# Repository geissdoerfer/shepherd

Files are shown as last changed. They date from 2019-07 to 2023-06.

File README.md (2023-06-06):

# SHEpHERD: SyncHronized Energy Harvesting Emulator RecorDer



DEPRECATION NOTICE:
This repository has been deprecated in favor of [the next generation of Shepherd](https://github.com/orgua/shepherd).

Batteryless sensor nodes depend on harvesting energy from their environment.
Developing solutions involving groups of batteryless nodes requires a tool to analyze, understand and replicate spatio-temporal harvesting conditions.
*shepherd* is a testbed for the batteryless Internet of Things, allowing to record harvesting conditions at multiple points in space over time.
The recorded data can be replayed to attached wireless sensor nodes, examining their behaviour under the constraints of spatio-temporal energy availability.

**Features**

 - High-speed, high resolution current and voltage sensing
 - Technology-agnostic: Currently, solar and kinetic energy harvesting are supported
 - Remote programming/debugging of ARM Cortex-M MCUs using Serial-Wire-Debug
 - High resolution, synchronized GPIO tracing
 - Configurable, constant voltage power supply for attached sensor nodes
 - Level-translated serial connection to the attached sensor nodes

For a detailed description see our [Paper](https://wwwpub.zih.tu-dresden.de/~mzimmerl/pubs/geissdoerfer19shepherd.pdf).

A *shepherd* instance consists of a group of spatially distributed *shepherd* nodes that are time-synchronized with each other.
Each *shepherd* node consists of a [BeagleBone](https://beagleboard.org/bone), the *shepherd* cape and a particular choice of capelets according to the user requirements.

This repository contains the hardware design files for the shepherd cape and the various capelets, the software running on each *shepherd* node as well as the tool to orchestrate a group of *shepherd* nodes connected to a network.

## Quickstart

Start by assembling your *shepherd* nodes, consisting of a BeagleBone Green/Black, a *shepherd* cape, a harvesting capelet and a target capelet.
The next step is to manually install the latest Ubuntu Linux on each BeagleBone.
You can install it to SD-card or the on-board EMMC flash, following [the official instructions](https://elinux.org/BeagleBoardUbuntu).
Make sure to follow the instructions for **BeagleBone**.

The following instructions describe how to install the *shepherd* software on a group of *shepherd* nodes connected to an Ethernet network.
We assume that your local machine is connected to the same network, that the nodes have internet access and that you know the IP address of each node.

If you haven't done it yet, clone this repository to your local machine:

```
git clone https://github.com/geissdoerfer/shepherd.git
```

Next, install the tools used for installing and controlling the *shepherd* nodes.
We'll use [Ansible](https://www.ansible.com/) to remotely roll out the basic configuration to each *shepherd* node and *shepherd-herd* to orchestrate recording/emulation across all nodes.
The tools are hosted on `PyPI` and require Python version >= 3.6.
You'll also need to have `sshpass` installed on your machine, which is available through the package management system of all major distributions.
Install the tools using `pip`:

```
pip3 install ansible shepherd-herd
```

The `inventory/herd.yml` file shows an example of how to provide the host names and known IP addresses of your BeagleBones.
Adjust it to reflect your setup.
You can arbitrarily choose and assign the hostnames (sheep0, sheep1, in this example) and the ansible_user (jane in this example).

```
sheep:
  hosts:
    sheep0:
        ansible_host: 192.168.1.100
    sheep1:
        ansible_host: 192.168.1.101
    sheep2:
        ansible_host: 192.168.1.102
  vars:
    ansible_user: jane
```

Now run the `bootstrap.yml` *Ansible* playbook, which sets the hostname, creates a user and enables passwordless ssh and sudo:

```
ansible-playbook deploy/bootstrap.yml
```

Finally, use the `install.yml` playbook to setup the *shepherd* software, optionally configuring PTP for time-synchronization:

```
ansible-playbook deploy/install.yml -e ptp=true
```

## Usage

Record two minutes of data:

```
shepherd-herd record -l 120 -o recording.h5
```
The command starts the recording asynchronously and returns after all nodes have started recording.
While the nodes are still recording (indicated by blinking of LED 1 and 2), prepare a directory on your local machine:

```
mkdir ~/shepherd_recordings
```

After the nodes stop blinking, you can retrieve the data to analyze it on your local machine:

```
shepherd-herd retrieve recording.h5 ~/shepherd_recordings
```

After installing some additional dependencies, you can use the provided command line utility from `extra/plot.py` to visualize the recorded data:

```
pip install numpy matplotlib h5py click
python extra/plot.py -f ~/shepherd_recordings/sheep1/rec.h5
```

For a detailed description of the [HDF5](https://en.wikipedia.org/wiki/Hierarchical_Data_Format) based data format, refer to the [corresponding documentation](https://shepherd-testbed.readthedocs.io/en/latest/user/data_format.html).

Finally, replay the previously recorded data to the attached sensor nodes, recording their power consumption:

```
shepherd-herd emulate -o consumption.h5 recording.h5
```

Try `shepherd-herd --help` or check out the documentation [here](https://shepherd-testbed.readthedocs.io/en/latest/user/cli.html#shepherd-herd) for a list of all options.

## Problems and Questions

*shepherd* is an early stage project and chances are that something is not working as expected.
Also, some features are not yet fully supported or documented.
If you experience issues or require additional features, please get in touch via e-mail or by creating an issue on github.

## Documentation

The documentation is hosted on [readthedocs](https://shepherd-testbed.readthedocs.io/en/latest/).

## People

*shepherd* development is lead at the Networked Embedded Systems Lab at TU Dresden as part of the DFG-funded project Next-IoT.

The following people have contributed to *shepherd*:

 - [Kai Geissdoerfer](https://www.researchgate.net/profile/Kai_Geissdoerfer)
 - [Mikolaj Chwalisz](https://www.tkn.tu-berlin.de/team/chwalisz/)
 - [Marco Zimmerling](https://wwwpub.zih.tu-dresden.de/~mzimmerl/)
 - [Justus Paulick](https://github.com/kugelbit)
 - [Boris Blokland](https://github.com/borro0)
 - [Ingmar Splitt](https://github.com/orgua)

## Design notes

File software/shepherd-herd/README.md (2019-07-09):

# shepherd-herd

*shepherd-herd* ist the command line utility for controlling a group of shepherd nodes remotely through an IP-based network.

## Installation

*shepherd-herd* is a pure python package and available on PyPI.
Use your python package manager to install it.
For example, using pip:

```
pip install shepherd-herd
```

## Usage

All *shepherd-herd* commands require the list of hosts on which to perform the requested action.
This list of hosts is provided with the `-i` option, that takes either the path to a file or a comma-separated list of hosts (compare Ansible `-i`).

For example, save the following file as `hosts`.

```
sheep:
  hosts:
    sheep0:
    sheep1:
    sheep2:
  vars:
    ansible_user: jane
```

Then use shepherd-herd to check if all your nodes are up:

```
shepherd-herd -i hosts run echo 'hello'
```

Or, equivalently define the list of hosts on the command line

```
shepherd-herd -i sheep0,sheep1,sheep2, run echo 'hello'
```

Here, we just provide a selected set of examples of how to use *shepherd-herd*.
For a full list of supported commands and options, run ```shepherd-herd --help``` and ```shepherd-herd [COMMAND] --help```.

Simultaneously start a 30s recording on the nodes defined in the `hosts` file:

```
shepherd-herd -i hosts record -o rec.h5
```

After recording is done, retrieve the data from all nodes and merge it to one hdf5 file on your local machine for analysis:

```
shepherd-herd -i hosts retrieve --merge -o rec_merged.h5 rec.h5
```

Flash a firmware image to the sensor nodes attached to the shepherd nodes:

```
shepherd-herd -i hosts target flash firmware_img.bin
```

Reset the sensor nodes:

```
shepherd-herd -i hosts target reset
```

Simultaneously start to play back the previously recorded data to the attached sensor nodes and monitor their power consumption and GPIO events:

```
shepherd-herd -i hosts emulate -i rec.h5 -o load.h5
```

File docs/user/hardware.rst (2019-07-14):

Hardware
========

Shepherd is a HW/SW solution and this section describes the key interfaces of the shepherd HW that are relevant to users.

Each shepherd node consists of 5 key components:

* The BeagleBone is a Single Board Computer, handling synchronization, data storage and hardware control
* The shepherd cape hosts the DC/DC converter, amplifiers and ADC, DAC and corresponding emulation circuitry and all other fixed hardware parts
* The harvesting capelet connects a harvesting transducer (e.g. solar panel) to the input of the DC/DC converter on the shepherd cape
* The target capelet connects a sensor node (e.g. a microcontroller with radio) to the capacity buffered output of the DC/DC converter on the shepherd cape
* The storage capelet hosts the capacitor used to temporarily store harvested energy during recording and emulation

Harvesting capelet
------------------

The harvesting capelet connects any type of harvester, e.g., a solar panel or piezo-electric element to the shepherd hardware.
By keeping this part of the hardware separate from the main shepherd cape, we allow to easily connect various types of harvesters, without having to change the complex and expensive main cape.

The harvesting capelet connects to the shepherd cape via three headers.
Two headers connect directly to the lower half of the pins of the P8 and P9 headers on the BeagleBone.
The third header is the custom, 4-pin connection between the capelet and the cape.

There are two reference harvesting capelets, one for solar harvesting (hardware/capelets/solar) and one for kinetic harvesting (hardware/capelets/kinetic).

.. table:: Header P1 pinout

    ========== =========================================
    Pin number Description
    ========== =========================================
    1          Ground
    2          Ground
    3          Input of DC/DC converter
    4          Input for setting MPP via voltage divider
    ========== =========================================

Target capelet
--------------

Shepherd provides a generic interface to connect any type of sensor node that can be supplied by emulated energy traces, while tracing its state with GPIO and UART.

The target capelet connects to the shepherd cape via three headers.
Two headers connect directly to the upper half of the pins of the P8 and P9 headers on the BeagleBone.
The third header is the custom, 16-pin connection between the capelet and the cape.

.. table:: Header P2 pinout

    ========== ====================================================================================
    Pin number Description
    ========== ====================================================================================
    1          Capacity buffered output of DC/DC converter
    2          Ground
    3          Battery voltage in operating range indicator
    4          High side of shunt resistor for harvesting current measurement
    5          +3.3V from BeagleBone LDO, use for any additional infrastructure circuitry
    6          Low side of shunt resistor for harvesting current measurement
    7          Ground
    8          GPIO2 - voltage translated digital signal from target to BeagleBone for tracing
    9          UART TX - voltage translated UART signal from target to Beaglebone UART1
    10         GPIO0 - voltage translated digital signal from target to BeagleBone for GPIO tracing
    11         UART RX - voltage translated UART signal from Beaglebone UART1 to target
    12         GPIO3 - voltage translated digital signal from target to BeagleBone for tracing
    13         SWDCLK - Clock line for remote programming via ARM Serial-Wire-Debug (SWD)
    14         GPIO1 - voltage translated digital signal from target to BeagleBone for tracing
    15         SWDIO - Data line for remote programming via ARM Serial-Wire-Debug (SWD)
    16         Ground
    ========== ====================================================================================

Pin 5 provides regulated 3.3V to supply any additional circuitry independent of the actual harvesting power supply.
This could be used to power, for example, a debugging LED that should not interfere with the energy emulation/measurement.
Pins 4 and 6 provide access to the voltage across the shunt resistor between the harvester/emulator and the DC/DC converter.
This allows to measure harvesting voltage and current online on the sensor node, which might be interesting for certain directions of research.
Pins 9 and 11 expose the level-translated signals to UART1 on BeagleBone. They can be used to trace UART messages from the target sensor node.
Pins 8, 10, 12, 14 are (level-translated) connected to the low-latency GPIOs that are sampled by shepherd software for GPIO tracing.
Pins 13 and 15 (level-translated) are used to program/debug a connected sensor node with SWD.

Storage capelet
---------------

Although less relevant for recording, the choice of capacitor crucially defines system behaviour during emulation.
Therefore, shepherd allows to easily swap the capacitor to experiment with different technologies/capacities by changing storage capelets.

The storage capelet directly connects the two ends of a mounted capacitor to the corresponding traces on the shepherd cape via two custom, 4-pin headers.

.. table:: Header P3 pinout

    ========== ===========================================================
    Pin number Description
    ========== ===========================================================
    1          +3.3V from BeagleBone LDO, use for any additional circuitry
    2          High side of capacitor
    3          Ground
    4          Ground
    ========== ===========================================================

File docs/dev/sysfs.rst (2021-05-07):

SYSFS interface
===============

The shepherd kernel module provides a user interface that exposes relevant parameters and allows control of the state of the underlying shepherd engine consisting of the kernel module and the firmware running on the two PRU cores. When the module is loaded, the interface is available under `/sys/shepherd`

- `n_buffers`: The maximum number of buffers used in the data exchange protocol
- `samples_per_buffer`: The number of samples contained in one buffer. Each sample consists of a current and a voltage value.
- `buffer_period_ns`: Time period of one 'buffer'. Defines the sampling rate togethere with `samples_per_buffer`
- `memory/address`: Physical address of the shared memory area that contains all `n_buffers` data buffers used to exchange data
- `memory/size`: Size of the shared memory area in bytes
- `sync/error_sum`: Integral of PID control error
- `sync/error`: Instantaneous PID control error
- `sync/correction`: PRU Clock correction (in ticks~5ns) as calculated by the PID controller

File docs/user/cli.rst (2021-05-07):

Command-line tools
==================

Shepherd offers two command line utilities:

`Shepherd-herd`_ is the command line utility for remotely controlling a group of shepherd nodes.
This is the key user interface to shepherd.
The pure-python package is installed on the user's local machine and sends commands to the shepherd nodes over *ssh*.

`Shepherd-sheep`_ is the command line utility for locally controlling a single shepherd node.
Depending on your use-case you may not even need to directly interact with it!

.. _shepherd-herd-cli:

shepherd-herd
-------------

.. click:: shepherd_herd:cli
   :prog: shepherd-herd
   :show-nested:

Examples
********

In the following we assume that you have an ansible style, YAML-formatted inventory file named `hosts` in your current working diretory.
Refer to the example `hosts` file in the root directory of the shepherd repository.
To start recording harvesting data using the hardware MPPT algorithm and store it under the default path, overwriting existing data and precharging the capacitor before starting the recording:

.. code-block:: bash

    shepherd-herd -i hosts record -f --init-charge

To stop recording on a subset of nodes (sheep1 and sheep3 in this example):

.. code-block:: bash

    shepherd-herd -i hosts -l sheep1,sheep3 stop

Another example for recording, this time with a fixed harvesting voltage of 600mV, limited recording duration of 30s and storing the result under `/var/shepherd/recordings/rec_v_fixed.h5`.
Also, instead of using the inventory file option, we specify hosts and ssh user on the command line:

.. code-block:: bash

    shepherd-herd -i sheep0,sheep1, -u jane record -d 30 --harvesting-voltage 0.6 -o rec_v_fixed.h5

To retrieve the recordings from the shepherd nodes and store them locally on your machine under the `recordings/` directory:

.. code-block:: bash

    shepherd-herd -i hosts retrieve -d rec_v_fixed.h5 recordings/

Before turning to emulation, here's how to flash a firmware image to the attached sensor nodes.
To flash the image `firmware.bin` that is stored on the local machine:

.. code-block:: bash

    shepherd-herd -i hosts target flash firmware.bin

To reset the CPU on the sensor nodes:

.. code-block:: bash

    shepherd-herd -i hosts target reset

Finally, to replay previously recorded data from the file `rec.h5` in the shepherd node's file system and store the recorded IV data from the load as `load.h5`:

.. code-block:: bash

    shepherd-herd -i hosts emulate -o load.h5 rec.h5

.. _shepherd-sheep-cli:

shepherd-sheep
--------------

.. click:: shepherd.cli:cli
   :prog: shepherd-sheep
   :show-nested:

Examples
********

Coming soon...

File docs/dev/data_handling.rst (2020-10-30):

Data handling
=============

Data Acquisition
----------------

Data is sampled/replayed through the ADC (TI ADS8694) and DAC (TI DAC8562T). Both devices are interfaced over a custom, SPI-compatible protocol. For a detailed description of the protocol and timing requirements, refer to the corresponding datasheets. The protocol is bit-banged using the low-latency GPIOs connected to PRU1. The transfer routines are implemented in assembly.

PRU to host
-----------

Data is sampled and transferred between PRUs and user space in buffers, i.e. blocks of SAMPLES_PER_BUFFER samples. These buffers correspond to sections of a continuous area of memory in DDR RAM to which both PRU and user space application have access. This memory is provisined through remoteproc, a Linux framework for managing resources in an AMP (asymmetric multicore processing) system. The PRU firmware contains a so-called resource table that allows to specify required resources. We request a carve-out memory area, which is a continuous, non-cached area in physical memory. On booting the PRU, the remoteproc driver reads the request, allocates the memory and writes the starting address of the allocated memory area to the resource table, which is readable by the PRU during run-time. The PRU exposes this memory location through shared RAM, which is accessible through the sysfs interface provided by the kernel module. Knowing physical address and size, the user space application can map that memory after which it has direct read/write access. The total memory areas is divided into N_BUFFERS distinct buffers.

In the following we describe the data transfer process for emulation. Emulation is the most general case because harvesting data has to be transferred from database to the analog frontend, while simultaneously consumption data (target voltage and current) has to be transferred from the analog frontend (ADC) to the database.

The userspace application writes the first block of harvesting data into one of the buffers, e.g. buffer index i. After the data is written, it sends an RPMSG to PRU1, indicating the message type (MSG_DEP_BUF_FROM_HOST) and index (i). The PRU receives that message and stores the index in a ringbuffer of empty buffers. When it's time, the PRU retrieves a buffer index from the ringbuffer and, sample by sample reads the harvesting values (current and voltage) from the buffer, sends it to the DAC and subsequently samples the 'load' ADC channels (current and voltage), overwriting the harvesting samples in the buffer. Once the buffer is full, the PRU sends an RPMSG with message type (MSG_DEP_BUF_FROM_PRU) and index (i). The userspace application receives the index, reads the buffer, writes its content to the database and fills it with the next block of harvesting data for emulation.

Data extraction
---------------

The user space code (written in python) has to extract the data from a buffer in the shared memory. Generally, a user space application can only access its own virtual address space. We use Linux's `/dev/mem` and python's `mmap.mmap(..)` to map the corresponding region of physical memory to the local address space. Using this mapping, we only need to seek the memory location of a buffer, extract the header information using `struct.unpack()` and interpret the raw data as numpy array using `numpy.frombuffer()`.

Database
--------

In the current implementation, all data is locally stored on SD-card. This means, that for emulation, the harvesting data is first copied to the corresponding shepherd node. The sampled data (harvesting data for recording and load data for emulation) is also stored on each individual node first and later copied and merged to a central database. We use the popular HDF5 data format to store data and meta-information.

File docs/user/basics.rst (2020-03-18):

Basics
======

*shepherd* is a testbed for the battery-less Internet of Things.
It allows to record harvesting conditions at multiple points in space over time.
The recorded data can be replayed to attached wireless sensor nodes, examining their behaviour under the constraints of spatio-temporal energy availability.

For a detailed description see our `Paper <https://wwwpub.zih.tu-dresden.de/~mzimmerl/pubs/geissdoerfer19shepherd.pdf>`_.

A *shepherd* instance consists of a group of spatially distributed *shepherd* nodes that are time-synchronized with each other.
Each *shepherd* node consists of a BeagleBone, the *shepherd* cape and a particular choice of capelets according to the user requirements.

Shepherd works in two key modes: `Recording`_ and `Emulation`_.
Through various digitally controlled analog switches, we can reconfigure the hardware according to the selected mode from software.

Time-synchronization
--------------------

Generally, shepherd can be used on a single node or without time-synchronization, for example, to measure the amount of energy that can be harvested in a particular scenario.
The more interesting feature however is that it enables to explore harvesting conditions across time and space, which is a crucial step towards collaboration and coordination of battery-less nodes.

For tethered settings, we propose to use the `Precision Time Protocol (PTP) <https://en.wikipedia.org/wiki/Precision_Time_Protocol>`_.
It requires that all shepherd nodes are connected to a common Ethernet network with as little switching jitter as possible.
The BeagleBone has hardware support for PTP and Linux provides the necessary tools.

In mobile or long-range scenarios, it might not be feasible to connect the nodes with Ethernet.
Instead, you can use the timing signal from a GPS receiver.
We have designed a GPS capelet (hardware/capelets/gps) to easily connect a GPS receiver and provide all necessary software in our repository.

Recording
---------

For recording, shepherd nodes are equipped with a harvesting transducer, e.g., a solar panel or piezo-electric harvester.
This transducer is connected to the input of the DC/DC boost converter on the shepherd cape.
The capacitor-buffered output of the DC/DC converter is connected to a *dummy load* that discharges the capacitor as soon as a threshold voltage is reached.
This is important, because the DC/DC converter can only charge a capacitor up to a maximum voltage before it switches off.
Shepherd measures the voltage and current on the input of the DC/DC converter.

A group of shepherd nodes can be deployed to the environment of interest to measure the energy that can be harvested at each node.
The time-synchronization between the shepherd nodes allows to gather the readings from multiple nodes with respect to a common time-line.
The data thus represents the spatio-temporal energy availability.

An important aspect of recording is the operating point of the DC/DC converter.
A harvesting transducer is characterized by its IV-curve, determining the magnitude of current at a specific load voltage.
The DC/DC boost converter can (within limits) regulate the input to a desired voltage, by adapting the current drawn from the transducer.
Thus, we have to inform the converter at which voltage we want to operate the transducer.
There are two options:

`Maximum Power Point Tracking (MPPT) <https://en.wikipedia.org/wiki/Maximum_Power_Point_Tracking>`_
***************************************************************************************************

The BQ25505 boost converter on the shepherd cape implements a simple MPPT algorithm in hardware.
In short, it disables the input every 16 seconds, samples the open circuit voltage and regulates its input voltage to a hardware-configurable fraction of that open circuit voltage.
Shepherd accounts for this by exposing the sampling input of the DC/DC converter to the harvesting capelet, such that the user can configure the voltage divider according to the specific type of harvester.
The low sampling rate of the algorithm makes it suitable only for slowly-changing harvesting conditions like solar energy.

User provided reference voltage
*******************************

A user can tell shepherd the voltage with which it should operate the harvester during recording.
Currently, the software only supports setting a constant voltage at the beginning of the recording.

Emulation
---------

In emulation mode, spatio-temporal current and voltage data is replayed to a group of sensor nodes.
Each shepherd node hosts a DAC controlled current source that can precisely set the current into the DC/DC converter.
The DC/DC converter has a reference voltage input that we use to set the voltage on its input.
With these two mechanisms, we are able to force the DC/DC converter into an arbitrary operating point.
Relying on time-synchronization, shepherd can thus faithfully reproduce previously recorded (or model-based) spatio-temporal energy conditions.

Instead of the dummy load, the capacitor-bufferd output of the DC/DC converter is connected to the target sensor node.
Thus, the sensor node is operated under the constraints of emulated energy availability.

Like other testbeds, shepherd records the voltage on the capacitor and the current consumed by the sensor node during emulation.
Furthermore, four GPIO lines and one bi-directional UART are level-translated between shepherd and the attached sensor node, allowing to trace

Remote programming/debugging
----------------------------

For convenient debugging and development, shepherd implements a fully functional Serial-Wire-Debug (SWD) debugger.
SWD is supported by most recent ARM Cortex-M corand allows flashing images and debugging the execution of code.
Older platforms typically provide a serial boot-loader, which can be used to flash images over the pre-mentioned UART connection.

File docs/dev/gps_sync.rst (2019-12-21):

GPS-Time-Synchronisation
========================

The ultimate goal is to precisely synchronize all Linux system clocks in the network to global time obtained from a GPS receiver.
Note how the following description traverses the clock hierarchy top-down starting with the GPS receiver down to the linux clock on the host node.

General Structure
-----------------

The master node is connected to a u-blox GPS receiver (shepherd-capelet), from which it receives a PPS signal via GPIO and global time via UART if the GPS-Modul has an position-fix.
One kernel module and two services work in concert to provide a grandmaster clock:

- ``pps_gmtimer`` (kernel module) timestamps edges on a GPIO pin with respect to an internal hardware timer on the AM335x and feeds the timestamps as a Linux pps device.
- ``gpsd`` talks to the GPS via a serial interface, parses the protocol and extracts timing information that is fed to the following service (chrony).
- ``chrony`` combines the global timing information from gpsd and the precise PPS signal from the pps device and synchronizes the Linux system clock to global GPS time.

Hardware setup
--------------

The GPS-capelet (see `hardware/capelets/gps`) is stacked on top of the shepherd cape or an attached harvesting capelet, respectively.

- The PPS signal is connected to Timer4 on pin P8_7
- The GPS-Uart is connect over UART2 on pins P9_21 and P9_22
- The currently used gps-chip is the u-blox SAM-M8Q

Configuring GNSS module
-----------------------

The u-blox GPS receiver can be configured to optimize its perfomance. To do this directly form the host node the python the python script: ``ubloxmsg_exchange`` was
written (see https://github.com/kugelbit/ubx-packet-exchange). The configuration files can be found under ``config_files``.  To this end the following configurations were set:

- SBAS was disabled for better timing information
- The stationary mode was enabled to get a better percussion and a stable perfomance
- the GPS- and galileo-satelite-systems were enabled to get a fast and stable fix

In addtion the standard config of the receiver leads to the following behaviour:

- If the PPS is not locked, the LED on the capelet will not blink. After the lock is attained, the LED will start blinking at 1 Hz.
- NMEA messages are enabled for the UART link which connects to the BeagleBone.

Deploy
------

Please use the ansible gps-host role.
``ansible-playbook deploy.yml``

Useful commands
---------------

Check if PPS pulses are coming: ``cat /sys/class/pps/pps0/assert``
On the master check that gpsd and chrony are running:

- ``systemctl status gpsd``
- ``systemctl status chrony``

gpsd comes with a command line client that display GPS data on the commandline: ``cgps``
Familiarize with chrony output:

- ``chronyc sources -v``
- ``chronyc sourcestats -v``
- ``chronyc tracking -v``

Configuration files:

- chrony: ``/etc/chrony/chrony.conf``
- gpsd: ``/etc/default/gpsd``
- the device tree file (dts) for the GPS-caplet is found in the pps-gmtimer folder (DD-GPS-00A0.dts).

DEBUG:
if you want to see whats going on you can run the services in DEBUG-Mode:

- chrony: ``sudo chronyd -dd``
- gpsd: ``sudo gpsd -N /dev/ttyO2 -D15 -n``

Pitfalls
--------
- For a good result (fast and stable fixes) it is very import to provide a clear sky view to the gps-caplet.
- The are lot of possible configuration options for the u-blox chip (see  SAM-M8Q Receiver Description) that may furthre optimize performance. For more research in this direction use the u-blox u-center software.
- The currently used u-blox chip does not support the u-blox time mode. This mode can increase the timing accuracy (see u-blox M8 Receiver Description).

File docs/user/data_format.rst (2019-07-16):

Data format
===========

Data is stored in the popular `Hierarchical Data Format <https://en.wikipedia.org/wiki/Hierarchical_Data_Format>`_.

This section describes the structure of data recorded with shepherd:

.. code-block:: text

    .
    |-- attributes
    |   `-- mode
    |-- data
    |   |-- time
    |   |-- current
    |   |   `-- attributes
    |   |       |-- gain
    |   |       `-- offset
    |   `-- voltage
    |       `-- attributes
    |           |-- gain
    |           `-- offset
    `-- gpio
        |-- time
        `-- values

The "mode" attribute allows to distinguish between "load" data and "harvesting" data.

The data group contains the actual IV data.
Time stores the time for each sample in nanoseconds.
Current and voltage store the binary data as acquired from the ADC.
They can be converted to their physical equivalent using the corresponding gain and offset attributes.
See also :doc:`calibration`.

The gpio group stores the timestamp when a GPIO edge was detected and the corresponding bit mask in values.
For example, assume that all are were low at the beginning of the recording.
At time T, GPIO pin 2 goes high.
The value 0x04 will be stored together with the timestamp T in nanoseconds.

There are numerous tools to work with HDF5 and library bindings for all popular programming languages.

Here's an example how to plot data recorded with shepherd using Python:

.. code-block:: python

    import h5py
    import matplotlib.pyplot as plt

    f, axarr = plt.subplots(1, 2)
    with h5py.File("rec.h5", "r") as hf:
        # convert time to seconds
        t = hf["data"]["time"][:].astype(float) / 1e9
        for i, var in enumerate(["voltage", "current"]):
            gain = hf["data"]["voltage"].attrs["gain"]
            offset = hf["data"]["voltage"].attrs["offset"]
            values = hf["data"][var][:] * gain + offset
            axarr[i].plot(t, values)

    plt.show()

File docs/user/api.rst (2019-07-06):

API
===

The shepherd API offers high level access to shepherd's functionality and forms the base for the two command line utilities.
Note that the API only convers local functionality on a single shepherd node.
Use the `shepherd-herd` command line utility to orchestrate a group of shepherd nodes remotely.

Recorder
--------

The recorder is used to configure all relevant hardware and software and to sample and extract data from the analog frontend.

.. autoclass:: shepherd.Recorder
   :members:
   :inherited-members:

Usage:

.. code-block:: python

    # Configure converter for fixed 1.5V input regulation
    with Recorder(harvesting_voltage=1.5) as recorder:
        recorder.start()

        for _ in range(100):
            idx, buf = recorder.get_buffer()
            recorder.release_buffer(idx)

Emulator
--------

The emulator is used to replay previously recorded IV data to an attached sensor node.

.. autoclass:: shepherd.Emulator
   :members:
   :inherited-members:

Usage:

.. code-block:: python

    # We'll read existing data using a LogReader
    lr = LogReader("mylog.h5")
    with ExitStack() as stack:
        stack.enter_context(lr)
        emu = Emulator(
            calibration_recording=lr.get_calibration_data(),
            initial_buffers=lr.read_buffers(end=64),
        )
        stack.enter_context(emu)
        emu.start()

        for hrvst_buf in lr.read_buffers(start=64):
            idx, _ = emu.get_buffer()
            emu.put_buffer(idx, hrvst_buf)

LogWriter
---------

The *LogWriter* is used to store IV data sampled with shepherd to an hdf5 file.

.. autoclass:: shepherd.LogWriter
   :members:

Usage:

.. code-block:: python

    with LogWriter("mylog.h5") as log_writer, Recorder() as recorder:
        recorder.start()
        for _ in range(100):
            idx, buf = recorder.get_buffer()
            log_writer.write_buffer(buf)
            recorder.release_buffer(idx)

LogReader
---------

The *LogReader* is used to read previously recorded data from an hdf5 file buffer by buffer.
It can be used with the Emulator to replay recorded data to an attached sensor node.

.. autoclass:: shepherd.LogReader
   :members:

Usage:

.. code-block:: python

    with LogReader("mylog.h5") as log_reader:
        for buf in log_reader.read_buffers(end=1000):
            print(len(buf))

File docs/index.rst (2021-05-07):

.. SHEPHERD documentation master file, created by
   sphinx-quickstart on Thu Jun 27 19:11:40 2019.
   You can adapt this file completely to your liking, but it should at least
   contain the root `toctree` directive.

Welcome to SHEPHERD's documentation!
====================================

To learn how *shepherd* enables research into the most challenging problems of coordinating battery-less sensor nodes, take a look at our `paper <https://wwwpub.zih.tu-dresden.de/~mzimmerl/pubs/geissdoerfer19shepherd.pdf>`_.
To get a basic understanding of what shepherd does, read the :doc:`user/basics`.
If you have the hardware on your desk and want to get started, read :doc:`user/getting_started`.
To record/emulate data on a group of shepherd nodes, use the :ref:`shepherd-herd-cli` command line utility.

User Guide
--------------

.. toctree::
   :maxdepth: 2

   user/basics
   user/getting_started
   user/hardware
   user/cli
   user/calibration
   user/data_format
   user/api
   user/performance

Developer Guide
---------------------

.. toctree::
   :maxdepth: 2

   dev/contributing
   dev/data_handling
   dev/sysfs
   dev/gps_sync

Indices and tables
==================

* :ref:`genindex`
* :ref:`modindex`
* :ref:`search`

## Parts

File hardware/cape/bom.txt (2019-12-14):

The BOM is hosted at: https://octopart.com/bom-tool/xuzBwsvQ

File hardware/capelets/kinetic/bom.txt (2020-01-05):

The BOM is hosted at: https://octopart.com/bom-tool/V1sd4P1T

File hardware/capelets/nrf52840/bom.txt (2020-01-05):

The BOM is hosted at: https://octopart.com/bom-tool/H5vysKdJ

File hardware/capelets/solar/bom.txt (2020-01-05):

The BOM is hosted at: https://octopart.com/bom-tool/nyzrF727

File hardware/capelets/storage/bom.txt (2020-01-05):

The BOM is hosted at: https://octopart.com/bom-tool/QGZYyQnQ

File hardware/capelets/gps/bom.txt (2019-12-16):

The BOM is hosted at: https://octopart.com/bom-tool/BEuSw9e5

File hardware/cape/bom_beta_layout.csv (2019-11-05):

BILL OF MATERIAL WITH BETA STOCK, GROUPED BY VALUES, AS OF 09.10.2015
Part | Value | Device | Package | Description | Description2 | Qty | Place_YES/NO | Povided_by_customer_YES/NO | Distributor | Ordernumber | Weblink | Remarks_customer | Unit_price | Total_price | REMARKS_BETA | OPTION1 | OPTION2 | OPTION3
C1, C2, C3, C6, C7, C8, C23, C27, C30, C31, C38, C45, C46, C48, C51 | 0.1u | C_SMD0402 | CAPC1005X55 |  |  | 15 | YES | NO | Beta | 7235228 | http://de.rs-online.com/web/p/ceramic-multilayer-capacitors/7235228P/?searchTerm=7235228p
C4, C5, C9, C24, C25, C29, C33, C34, C47, C49 | 1n | C_SMD0402 | CAPC1005X55 |  |  | 10 | YES | NO | Beta | 147566 | http://de.rs-online.com/web/p/keramik-multilayer-kondensatoren/0147566/?searchTerm=147566
C10 | 2.2n | C_SMD0402 | CAPC1005X55 |  |  | 1 | YES | NO | Digi-Key | 399-3068-1-ND | https://www.digikey.com/products/en?keywords=399-3068-1-ND
C11, C12, C13, C18, C21 | 10u | C_SMD0805 | CAPC2012X145 |  |  | 5 | YES | NO | Beta | 6911161P | http://uk.rs-online.com/web/search/searchBrowseAction.html?method=searchProducts&searchTerm=6911161P&x=0&y=0
C14, C15, C16, C19, C20, C22, C26, C28, C32, C35 | 1u | C_SMD0603 | CAPC1608X95 |  |  | 10 | YES | NO | Beta | 6911142 | http://de.rs-online.com/web/p/keramik-multilayer-kondensatoren/6911142/?searchTerm=6911142
C17 | 22u | C_SMD1210 | CAPC3225X280 |  |  | 1 | YES | NO | Digi-Key | 399-7451-1-ND | https://www.digikey.com/products/en?keywords=399-7451-1-ND
C36, C39, C40 | 2.2u | C_SMD0805 | CAPC2012X145 |  |  | 3 | YES | NO | Digi-Key | 1276-2956-1-ND | https://www.digikey.com/products/en?keywords=1276-2956-1-ND
C37 | 0.47u | C_SMD0603 | CAPC1608X95 |  |  | 1 | YES | NO | Digi-Key | 399-7934-1-ND | https://www.digikey.com/products/en?keywords=399-7934-1-ND
C41, C43, C44 | 4.7u | C_SMD0805 | CAPC2012X145 |  |  | 3 | YES | NO | Beta | 6911186P | http://uk.rs-online.com/web/search/searchBrowseAction.html?method=searchProducts&searchTerm=6911186P&x=0&y=0
C42, C50 | 10n | C_SMD0402 | CAPC1005X55 |  |  | 2 | YES | NO | Beta | 147049 | http://de.rs-online.com/web/p/keramik-multilayer-kondensatoren/0147049/?searchTerm=147049
D1, D2 | BAT43WS-HE3SOD-323 | BAT43WS-HE3SOD-323 | SOD2513X110 |  |  | 2 | YES | NO | Digi-Key | BAT43WS-HE3-08GICT-ND | https://www.digikey.com/products/en?keywords=BAT43WS-HE3-08GICT-ND
D3 | BZX384B5V1 | BZX384B5V1 | SOD2513X110 |  |  | 1 | YES | NO | Digi-Key | BZX384C5V1-HE3-08GICT-ND | https://www.digikey.com/products/en?keywords=BZX384C5V1-HE3-08GICT-ND
D4, D5, D6, D7 | ACDBQC0130L-HF0402 | ACDBQC0130L-HF0402 | DIOC0905X50N |  |  | 4 | YES | NO | Digi-Key | 641-2041-1-ND | https://www.digikey.com/products/en?keywords=641-2041-1-ND
IC1, IC3 | AD8422BRMZ | AD8422BRMZ | RM_8-L |  |  | 2 | YES | NO | Digi-Key | AD8422ARMZ-ND | https://www.digikey.com/products/en?keywords=AD8422ARMZ-ND
IC2, IC4, IC6 | OPA2388DGK8_L | OPA2388DGK8_L | DGK8-L |  |  | 3 | YES | NO | Digi-Key | 296-50277-1-ND | https://www.digikey.com/products/en?keywords=296-50277-1-ND
IC5 | ADS8694TSSOP38 | ADS8694TSSOP38 | TSSOP38 |  |  | 1 | YES | NO | Digi-Key | 296-42531-5-ND | https://www.digikey.com/products/en?keywords=296-42531-5-ND
IC7 | DAC6571IDBVR | DAC6571IDBVR | DAC6571IDBVR |  |  | 1 | YES | NO | Digi-Key | 296-48525-1-ND | https://www.digikey.com/products/en?keywords=296-48525-1-ND
IC8 | TPS73101DBVR | TPS73101DBVR | SOT95P280X145-5N | Cap-Free, NMOS, 400mA Low-Dropout Regulator with Reverse Current Protection |  | 1 | YES | NO | Digi-Key | 296-27058-1-ND | https://www.digikey.com/products/en?keywords=296-27058-1-ND
IC9, IC15 | LMP7701MF | LMP7701MF | DBV5-L |  |  | 2 | YES | NO | Digi-Key | LMP7701MF/NOPBCT-ND | https://www.digikey.com/products/en?keywords=LMP7701MF/NOPBCT-ND
IC10 | DAC8562_DGS_10 | DAC8562_DGS_10 | DGS10 |  |  | 1 | YES | NO | Digi-Key | 296-43693-1-ND | https://www.digikey.com/products/en?keywords=296-43693-1-ND
IC11 | CAT24C256WI-GT3 | CAT24C256WI-GT3 | SO08 |  |  | 1 | YES | NO | Digi-Key | CAT24C256WI-GT3OSCT-ND | https://www.digikey.com/products/en?keywords=CAT24C256WI-GT3OSCT-ND
IC12 | LM27762DSSR | LM27762DSSR | VREG_LM27762DSSR | Low-Noise Positive- and Negative-Output Charge Pump With Integrated LDO 12-WSON -40 to 85 |  | 1 | YES | NO | Digi-Key | 296-44944-1-ND | https://www.digikey.com/products/en?keywords=296-44944-1-ND
IC13 | BQ25504_RGT_16 | BQ25504_RGT_16 | RGT16_1P7X1P7 |  |  | 1 | YES | NO | Digi-Key | 296-29741-1-ND | https://www.digikey.com/products/en?keywords=296-29741-1-ND
IC14 | SN74LV4T125PWR | SN74LV4T125PWR | PW0014A_N |  |  | 1 | YES | NO | Digi-Key | 296-40545-1-ND | https://www.digikey.com/products/en?keywords=296-40545-1-ND
IC16 | TXB0304RUTR | TXB0304RUTR | RUT0012A |  |  | 1 | YES | NO | Digi-Key | 296-29682-1-ND | https://www.digikey.com/products/en?keywords=296-29682-1-ND
JP1, JP2 |  | PINHD-1X2 | 1X02 | PIN HEADER |  | 2 | YES | NO | Digi-Key | 732-5315-ND | https://www.digikey.com/products/en?keywords=732-5315-ND
K1 | G3VM-31HR22SOP | G3VM-31HR22SOP | SOP06 | PhotoMOS Relay NAiS |  | 1 | YES | NO | Digi-Key | Z8598-ND | https://www.digikey.com/products/en?keywords=Z8598-ND
L1 | 22u | L-EUL3225P | L3225P | INDUCTOR, European symbol |  | 1 | YES | NO | Digi-Key | 732-7315-1-ND | https://www.digikey.com/products/en?keywords=732-7315-1-ND
LED1, LED2, LED3, LED4 | 598-8130-107FLED_0805 | 598-8130-107FLED_0805 | LEDC2012X75 |  |  | 4 | YES | NO | Digi-Key | 350-2040-1-ND | https://www.digikey.com/products/en?keywords=350-2040-1-ND
P1 |  | FE02-2 | FE02-2 | FEMALE HEADER |  | 1 | YES | NO | Digi-Key | SAM1212-02-ND | https://www.digikey.com/products/en?keywords=SAM1212-02-ND
P2 |  | FE08-2 | FE08-2 | FEMALE HEADER |  | 1 | YES | NO | Digi-Key | SAM1212-08-ND | https://www.digikey.com/products/en?keywords=SAM1212-08-ND
P3, P4 |  | FE04-1 | FE04-1 | FEMALE HEADER |  | 2 | YES | NO | Digi-Key | SAM1213-04-ND | https://www.digikey.com/products/en?keywords=SAM1213-04-ND
P8, P9 |  | FE23-2 | FE23-2 | FEMALE HEADER |  | 2 | YES | NO | Digi-Key | SAM1204-23-ND | https://www.digikey.com/products/en?keywords=SAM1204-23-ND
R1, R12, R15 | 402 | R_SMD0603 | RESC1608X55 |  |  | 3 | YES | NO | Digi-Key | P19926CT-ND | https://www.digikey.com/products/en?keywords=P19926CT-ND
R2, R11 | 2 | R_SMD0603 | RESC1608X55 |  |  | 2 | YES | NO | Digi-Key | A102258CT-ND | https://www.digikey.com/products/en?keywords=A102258CT-ND
R3, R20, R21, R51 | 24 | R_SMD0402 | RESC1005X40 |  |  | 4 | YES | NO | Digi-Key | YAG3073CT-ND | https://www.digikey.com/products/en?keywords=YAG3073CT-ND
R4 | 2.4k | R_SMD0402 | RESC1005X40 |  |  | 1 | YES | NO | Digi-Key | 311-2.40KLRCT-ND | https://www.digikey.com/products/en?keywords=311-2.40KLRCT-ND
R5 | 3.6k | R_SMD0402 | RESC1005X40 |  |  | 1 | YES | NO | Digi-Key | 311-3.6KLRCT-ND | https://www.digikey.com/products/en?keywords=311-3.6KLRCT-ND
R6, R7, R14, R17, R31, R50, R52 | 10k | R_SMD0402 | RESC1005X40 |  |  | 7 | YES | NO | Beta | 618-5832 | http://de.rs-online.com/web/p/products/6185832/?searchTerm=618-5832
R8, R16, R28, R30 | 1.2k | R_SMD0402 | RESC1005X40 |  |  | 4 | YES | NO | Beta | 618-6138 | http://de.rs-online.com/web/p/products/6186138/?searchTerm=618-6138
R9 | 91 | R_SMD0603 | RESC1608X55 |  |  | 1 | YES | NO | Digi-Key | 311-91.0HRCT-ND | https://www.digikey.com/products/en?keywords=311-91.0HRCT-ND
R10, R13, R18, R41, R42 | 220 | R_SMD0603 | RESC1608X55 |  |  | 5 | YES | NO | Beta | 6979191 | http://uk.rs-online.com/web/search/searchBrowseAction.html?method=getProduct&R=6979191
R19 | 30 | R_SMD0402 | RESC1005X40 |  |  | 1 | YES | NO | Digi-Key | A102788CT-ND | https://www.digikey.com/products/en?keywords=A102788CT-ND
R22, R23, R47, R48, R49 | 5.6k | R_SMD0402 | RESC1005X40 |  |  | 5 | YES | NO | Beta | 698-0693 | http://de.rs-online.com/web/p/products/6980693/?searchTerm=698-0693
R24 | 56k | R_SMD0402 | RESC1005X40 |  |  | 1 | YES | NO | Beta | 698-6761 | http://de.rs-online.com/web/p/products/6986761/?searchTerm=698-6761
R25 | 40.2k | R_SMD0402 | RESC1005X40 |  |  | 1 | YES | NO | Digi-Key | 311-40.2KLRCT-ND | https://www.digikey.com/products/en?keywords=311-40.2KLRCT-ND
R26 | 30k | R_SMD0402 | RESC1005X40 |  |  | 1 | YES | NO | Digi-Key | 311-30.0KLRCT-ND | https://www.digikey.com/products/en?keywords=311-30.0KLRCT-ND
R27, R29, R44, R46 | 100k | R_SMD0402 | RESC1005X40 |  |  | 4 | YES | NO | Beta | 6986783 | http://uk.rs-online.com/web/search/searchBrowseAction.html?method=getProduct&R=6986783
R32, R33, R34, R35, R36, R37, R38, R39, R40 | 510 | R_SMD0402 | RESC1005X40 |  |  | 9 | YES | NO | Beta | 698-0599 | http://de.rs-online.com/web/p/smd-widerstande/6980599/?searchTerm=698-0599
R43 | 300k | R_SMD0402 | RESC1005X40 |  |  | 1 | YES | NO | Digi-Key | 311-300KLRCT-ND | https://www.digikey.com/products/en?keywords=311-300KLRCT-ND
R45 | 294k | R_SMD0402 | RESC1005X40 |  |  | 1 | YES | NO | Digi-Key | YAG3092CT-ND | https://www.digikey.com/products/en?keywords=YAG3092CT-ND
ROK1, ROK2, ROV1, ROV2, RUV1 | 5.62M | R_SMD0603 | RESC1608X55 |  |  | 5 | YES | NO | Digi-Key | 541-5.62MHCT-ND | https://www.digikey.com/products/en?keywords=541-5.62MHCT-ND
ROK3 | 1.87M | R_SMD0603 | RESC1608X55 |  |  | 1 | YES | NO | Digi-Key | RMCF0603FT1M87CT-ND | https://www.digikey.com/products/en?keywords=RMCF0603FT1M87CT-ND
RUV2 | 3.6M | R_SMD0603 | RESC1608X55 |  |  | 1 | YES | NO | Digi-Key | RMCF0603FT3M60CT-ND | https://www.digikey.com/products/en?keywords=RMCF0603FT3M60CT-ND
S1 | ADG849YKSZ-REELKS_6-L | ADG849YKSZ-REELKS_6-L | KS_6-L |  |  | 1 | YES | NO | Digi-Key | ADG849YKSZ500RLCT-ND | https://www.digikey.com/products/en?keywords=ADG849YKSZ500RLCT-ND
S2 | ADG736LBRMZRM_10-L | ADG736LBRMZRM_10-L | RM_10-L |  |  | 1 | YES | NO | Digi-Key | ADG736LBRMZ-ND | https://www.digikey.com/products/en?keywords=ADG736LBRMZ-ND
T1, T2, T3, T5, T6 | SI2374DSSOT23-VSHAY | SI2374DSSOT23-VSHAY | SOT95P237X112-3 |  |  | 5 | YES | NO | Digi-Key | SI2374DS-T1-GE3CT-ND | https://www.digikey.com/products/en?keywords=SI2374DS-T1-GE3CT-ND
T4 | SI2307SOT23-VSHAY | SI2307SOT23-VSHAY | SOT95P237X112-3 |  |  | 1 | YES | NO | Digi-Key | SI2307BDS-T1-GE3CT-ND | https://www.digikey.com/products/en?keywords=SI2307BDS-T1-GE3CT-ND
TP1, TP2, TP3, TP4, TP5, TP6, WP | TPSQTP06R | TPSQTP06R | TP06R | Test pad |  | 7 | NO | NO

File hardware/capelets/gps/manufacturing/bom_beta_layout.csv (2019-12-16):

BILL OF MATERIAL WITH BETA STOCK, GROUPED BY VALUES, AS OF 09.10.2015
Part | Value | Device | Package | Description | Description2 | Qty | Place_YES/NO | Povided_by_customer_YES/NO | Distributor | Ordernumber | Weblink | Remarks_customer | Unit_price | Total_price | REMARKS_BETA | OPTION1 | OPTION2 | OPTION3
C1 | 22u | C_SMD1210 | CAPC3225X280 |  |  | 1 | YES | NO | Digi-Key | 399-7451-1-ND‎ | https://www.digikey.com/product-detail/en/C1210C226M4RACTU/399-7451-1-ND/3317485/?itemSeq=312440191
C2, C3 | 0.1u | C_SMD0805 | CAPC2012X145 |  |  | 2 | YES | NO | Beta | 2644422P | http://uk.rs-online.com/web/search/searchBrowseAction.html?method=searchProducts&searchTerm=2644422P&x=26&y=20
IC1 | SAM-M8Q | SAM-M8Q | SAM-M8Q | u-blox SAM GNSS antenna module |  | 1 | YES | NO | Digi-Key | 672-1054-1-ND‎ | https://www.digikey.com/product-detail/en/SAM-M8Q-0-10/672-1054-1-ND/7393573/?itemSeq=312440192
P8, P9 |  | PINHD-2X11 | 2X11 | PIN HEADER |  | 2 | YES | NO | Digi-Key | 3M156386-22-ND | https://www.digikey.de/products/en?keywords=%20929836-01-11-RK%20
PPS | 598-8130-107FLED_0805 | 598-8130-107FLED_0805 | LEDC2012X75 |  |  | 1 | YES | NO | Digi-Key | 350-2040-1-ND‎ | https://www.digikey.com/product-detail/en/5988130107F/350-2040-1-ND/1291344/?itemSeq=312440189
R1 | 130R | R_SMD0805 | RESC2012X65 |  |  | 1 | YES | NO | Beta | 6980003 | http://de.rs-online.com/web/search/searchBrowseAction.html?method=searchProducts&searchTerm=6980003&x=25&y=13
T1 | SI2374DSSOT23-VSHAY | SI2374DSSOT23-VSHAY | SOT95P237X112-3 |  |  | 1 | YES | NO | Digi-Key | SI2374DS-T1-GE3CT-ND‎ | https://www.digikey.com/product-detail/en/SI2374DS-T1-GE3/SI2374DS-T1-GE3CT-ND/6595036/?itemSeq=312440193

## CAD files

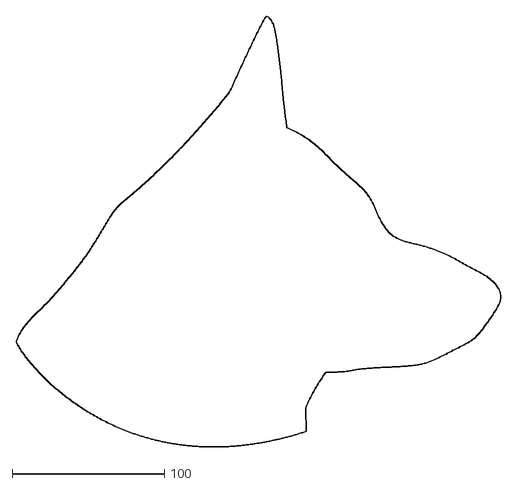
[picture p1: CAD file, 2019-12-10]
extra/logo.dxf
318.8 x 283.5

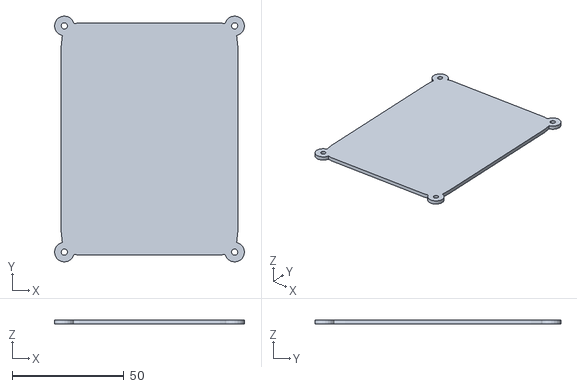
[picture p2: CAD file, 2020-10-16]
hardware/housing/harvester/piezo_harvester_cover.stl
85.0 x 110.0 x 2.00

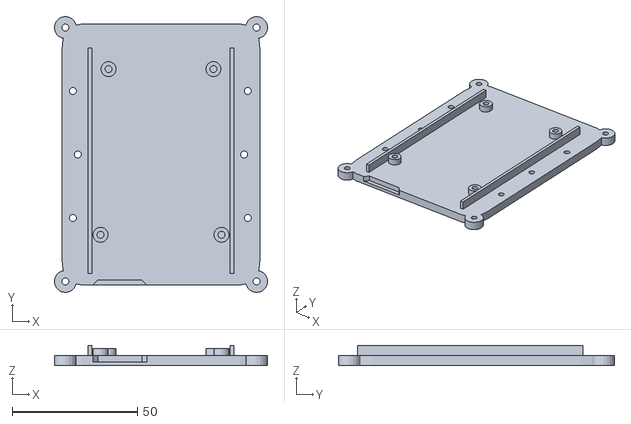
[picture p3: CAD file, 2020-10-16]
hardware/housing/shepherd/shepherd_plate.stl
85.0 x 110.0 x 8.00

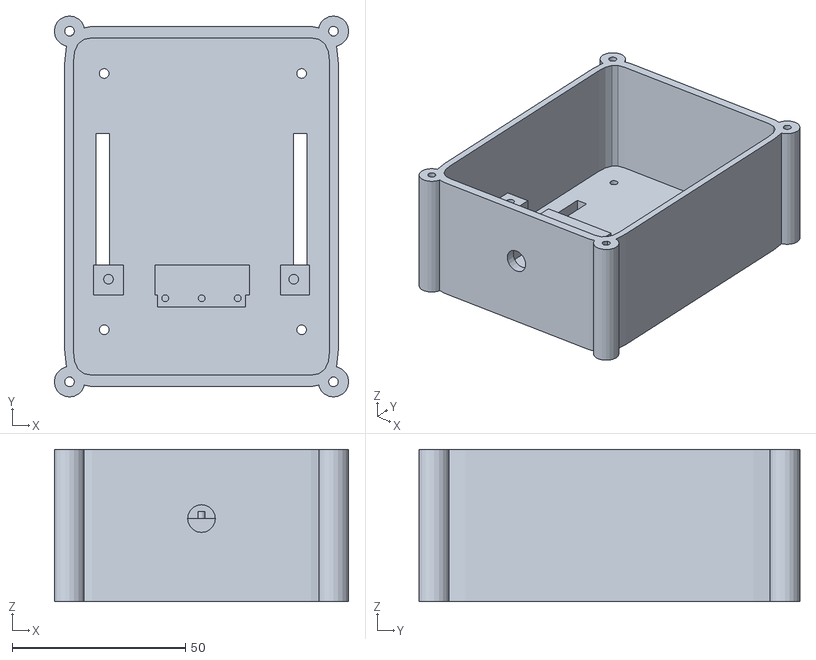
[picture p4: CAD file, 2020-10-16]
hardware/housing/harvester/piezo_harvester_case.stl
85.0 x 110.0 x 44.0

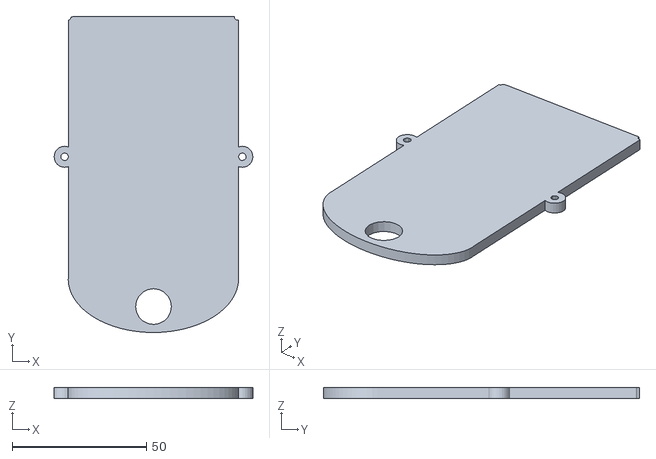
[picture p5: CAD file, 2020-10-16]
hardware/housing/shepherd/shepherd_cover.stl
74.0 x 117.6 x 4.00

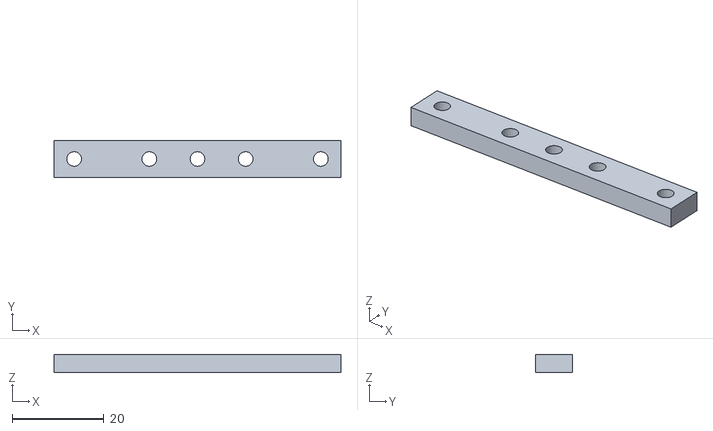
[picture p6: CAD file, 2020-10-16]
hardware/housing/harvester/piezo_harvester_clamp.stl
62.5 x 8.00 x 4.00

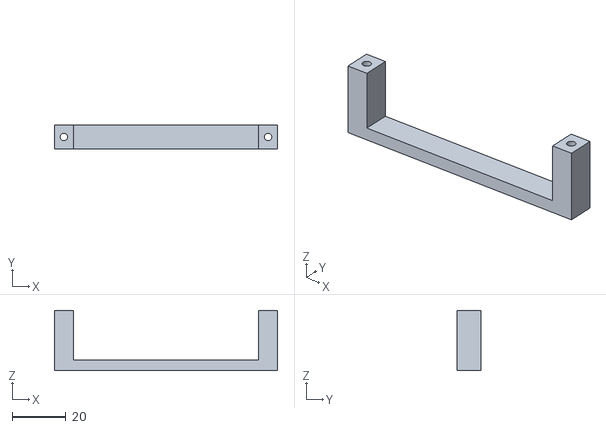
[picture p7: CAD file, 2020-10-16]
hardware/housing/shepherd/clamp_powerbank_belt.stl
83.0 x 8.80 x 22.5

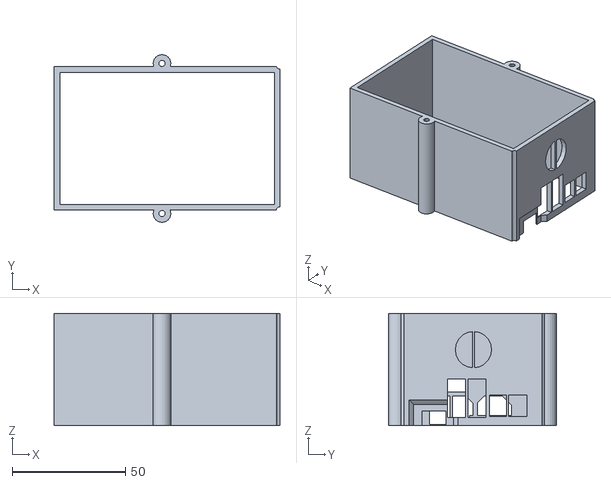
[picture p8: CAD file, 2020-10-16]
hardware/housing/shepherd/shpherd_wall.stl
99.6 x 74.0 x 49.5

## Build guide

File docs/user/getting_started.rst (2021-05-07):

Getting started
===============

This section describes how to setup an instance of shepherd in a tethered setup.

Prerequisites
-------------

To setup an instance of shepherd, you'll need to assemble a number shepherd nodes.

For each shepherd node, you'll need:

* BeagleBone (Green/Black)
* shepherd cape
* storage capelet

  * for recording: harvesting capelet and transducer, e.g. solar capelt and solar cell
  * for emulation: target capelet

In addition, you'll need at least one SD-card with at least 4GB capacity.

For the cape and capelets take a look at the `hardware design files <https://github.com/geissdoerfer/shepherd/tree/master/hardware>`_
The capelets can easily be soldered by hand.
The shepherd cape has a large number of small components and we suggest to send it to a PCB fab for assembly.

Place a capacitor of desired capacity on your storage capelets.
The reference layout offers a choice of three footprints allowing to flexibly choose a suitable capacitor and package.

If you don't have the necessary resource or need assistance with getting the hardware manufactured, get in touch with the developers.

To connect the shepherd nodes to each other for control, data collection and time-synchronization, you need to setup an Ethernet network.
The network should be as flat as possible, i.e. have a minimum number of switches.
By default, the BeagleBone Ubuntu image is configured to request an IP address by DHCP.
Therefore your network should have a DHCP server.

Hardware setup
--------------

Stack the cape on top of the BeagleBone.
Make sure to close the jumpers JP1 and JP2 on the cape.

Mount the storage capelet on headers P3/P4 on the cape.

Stack the harvesting capelet on top of the shepherd cape.
The two 11x2 headers of the capelet plug into the lower part (P8_1 - P8_22 and P9_1 - P9_22) of the 23x2 headers of the shepherd cape.
Pay attention to header P1 for the correct orientation.

Stack the target capelet on top of the shepherd cape.
The two 11x2 headers of the capelet plug into the upper part (P8_25 - P8_46 and P9_25 - P9_46) of the 23x2 headers of the shepherd cape.
Pay attention to header P2 for the correct orientation.

Provide all BeagleBones with power through the micro USB ports and connect their Ethernet ports to an Ethernet switch.
Using a PoE switch and corresponding micro USB power splitters can greatly reduce the cabling requirements.

The DHCP server and your machine (for installation/control) must be connected to the same network.

Installation
------------

Prepare the SD-cards.
If you plan to install the OS and shepherd software on the onboard EMMC flash, you can prepare one SD card and sequentially flash the nodes.
If you plan to install the OS and shepherd software on SD card, you have to prepare one SD card for every shepherd node.
Depending on your choice, follow `the official instructions <https://elinux.org/BeagleBoardUbuntu>`_ for **BeagleBone**.
Shepherd has been tested on Ubuntu 18.04 LTS, but might work with other Debian based distributions.

After installing the OS on the BeagleBones and booting them, find out their IP addresses.
If you know the subnet, you can use nmap from your machine, for example:

.. code-block:: bash

    nmap 192.168.178.0/24

Clone the shepherd repository to your machine:

.. code-block:: bash

    git clone https://github.com/geissdoerfer/shepherd.git

Add an inventory file in the `inventory` folder in the repository, assigning hostnames to the IP addresses of the shepherd nodes.
Just start by editing the provided `inventory/herd.yml` example.
Pick a username that you want to use to login to the nodes and assign as `ansible_user` variable.

.. code-block:: yaml

    sheep:
      hosts:
        sheep0:
          ansible_host: 192.168.1.100
        sheep1:
          ansible_host: 192.168.1.101
        sheep2:
          ansible_host: 192.168.1.102
      vars:
        ansible_user: jane

We'll use `Ansible <https://www.ansible.com/>`_ to roll out a basic configuration to the nodes.
This includes setting the hostname, adding the user, allowing password-less ssh access and sudo without password.
Make sure that you have `Python >=3.6`, `pip` and `sshpass` installed on your machine.
Install `Ansible` with:

.. code-block:: bash

    pip3 install ansible

Now run the *bootstrap* `Ansible playbook <https://docs.ansible.com/ansible/latest/user_guide/playbooks_intro.html>`_ using the previously prepared inventory file:

.. code-block:: bash

    ansible-playbook deploy/bootstrap.yml

To streamline the installation and upgrading process, the shepherd software is packaged and distributed as debian packages.
Installing is as easy as adding the shepherd repository to the aptitude sources and installing the shepherd metapackage.
The *install* playbook allows to easily automate this process on a group of nodes.

.. code-block:: bash

    ansible-playbook deploy/install.yml

To install and configure PTP for time-synchronizing a bunch of shepherd-nodes, you can set the `ptp` variable on the command line, alternatively you get asked on script-start:

.. code-block:: bash

    ansible-playbook deploy/install.yml -e "ptp=True"

On success, the nodes will reboot and should be ready for use, for example, using the *shepherd-herd* command line utility.

Further playbooks:
    - ``setup_linux_configuration.yml`` will handle updates, some configuration, remove clutter, improve ram-usage and boot-duration
    - ``setup_linux_performance.yml`` handles additional speed-improving changes
    - ``setup_linux_security.yml`` will close system so that nodes can be distributed safely in open spaces (basic steps against getting into system)
    - ``fetch-hostkeys.yml`` will copy keys from nodes, handy for reflashing image, while keeping keys
    - ``setup-dev-nfs.yml`` establish a local network file system ``/opt/shepherd-dev`` for the nodes to access
    - ``setup-ext-storage.yml`` will format and automount sd-card to ''/var/shepherd/recordings''
    - ``deploy.yml`` offers faster and easier way to test updates in shepherd-code-base
    - ``dev_rebuild_pru.yml`` hot-swaps pru-firmware (& kernel-module & py-package) by compiling and flashing without restart

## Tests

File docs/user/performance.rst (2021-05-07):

Performance Specification
=========================

The `Performance specification`_ table summarizes shepherd's key performance metrics.
Refer to our paper for a detailed description of how these values were obtained.
Some of the values were measured with an early prototype and may not accurately reflect the current hardware revision.

.. table:: Performance specification

    +----------------------------+------------------------+----------------------+
    | Range                      | Harvesting voltage     | 100 mV - 4.8 V       |
    +                            +------------------------+----------------------+
    |                            | Harvesting current     | 0 mA - 25 mA         |
    +                            +------------------------+----------------------+
    |                            | Load voltage           | 0 V - 4.8 V          |
    +                            +------------------------+----------------------+
    |                            | Load current           | 0 mA - 25 mA         |
    +                            +------------------------+----------------------+
    |                            | Emulation voltage      | 100 mV - 4 V         |
    +                            +------------------------+----------------------+
    |                            | Emulation current      | 0 mA - 25 mA         |
    +----------------------------+------------------------+----------------------+
    | 24h DC Accuracy            | Harvesting voltage     | 19.53 uV +/- 0.01 %  |
    +                            +------------------------+----------------------+
    |                            | Harvesting current     | 190 nA +/- 0.07 %    |
    +                            +------------------------+----------------------+
    |                            | Load voltage           | 19.53 uV +/- 0.01 %  |
    +                            +------------------------+----------------------+
    |                            | Load current           | 190 nA +/- 0.01 %    |
    +                            +------------------------+----------------------+
    |                            | Emulation voltage      | 76.3 uV +/- 0.012 %  |
    +                            +------------------------+----------------------+
    |                            | Emulation current      | 381.4 uA +/- 0.025 % |
    +----------------------------+------------------------+----------------------+
    | Bandwidth                  | All recording channels | 15 kHz               |
    +----------------------------+------------------------+----------------------+
    | Risetime                   | Emulation voltage      | 64 ms                |
    +                            +------------------------+----------------------+
    |                            | Emulation current      | 19.2 us              |
    +----------------------------+------------------------+----------------------+
    | Max. Burden voltage        | Harvesting recorder    | 50.4 mV              |
    +                            +------------------------+----------------------+
    |                            | Load recorder          | 76.1 mV              |
    +----------------------------+------------------------+----------------------+
    | GPIO sampling speed        |                        | 580 kHz - 5 MHz      |
    +----------------------------+------------------------+----------------------+
    | Power consumption          |                        | 345 mA               |
    +----------------------------+------------------------+----------------------+
    | Max. Synchronization error |                        | < 1.0 us             |
    +----------------------------+------------------------+----------------------+

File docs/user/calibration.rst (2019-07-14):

Calibration
===========

Data recorded with shepherd are stored in the database as raw binary values, read from the ADC.
In order to make sense of that data, we need to map the binary values to physical voltage and current values.
Similarly, for emulation, we need to map phyiscal voltage and current values to binary values that can be fed to the DAC.

This mapping is assumed to be linear.
For example, to convert a binary value :math:`v_{binary}` to its physical equivalent :math:`v_{physical}`:

.. math::

    v_{physical} = v_{binary} \cdot gain + offset

There are three "channels" and two "variables": harvesting, load and emulation, each with voltage and current.
Thus the complete set of calibration values consists of 12 values.
When storing recorded data, these values are stored together with the binary data.

The *gain* and *offset* values can be derived from nominal hardware configuration.
However, due to component tolerances, offset voltages and other effects, the real mapping can significantly differ from nominal values.

Therefore, we recommend to *calibrate* shepherd by comparing a number of sample points recorded with shepherd to known refernce values measured with accurate lab equipment.
From the tuples of reference values and measurements, you can estimate the *gain* and *offset* by ordinary least squares linear regression.
These values can be stored in the EEPROM on the shepherd cape and, at the beginning of a recording extracted and stored in the database file.

Support for an automated calibration procedure with *shepherd-herd* will be added soon.

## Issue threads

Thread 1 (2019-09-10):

### ISSUE TITLE
Disabling Comment in Sync Loop causes Timeout

### ISSUE THREAD

**Issue by borro0** [geissdoerfer/shepherd#1]
Since this log is kinda floading the kernel logs I wanted to comment it out, but that causes a timeout while running record:

https://github.com/geissdoerfer/shepherd/blob/71f0624637a9a549263fcd4fd6a18b1bf8253908/software/kernel-module/src/sync_ctrl.c#L156-L157

Result when code is commented out

command used: sudo python3 cli.py record -l 3
error:
shepherd.sysfs_interface.SysfsInterfaceException: timed out waiting for state running - state is idle

dmesg | grep shepherd:

[  845.073347] shepherd virtio1.rpmsg-shprd.-1.1: timeout waiting for a tx buffer
[  845.080691] shepherd virtio1.rpmsg-shprd.-1.1: rpmsg_send failed: -512

**Comment by geissdoerfer** [comment]
Thanks for reporting. I couldn't reproduce the issue, i.e. everything was working even after removing the print statement for me. Anyway, you're right that the messages flood kernel logs. This has been fixed with 7afac7eba10fd3febe215942e3e14bbce26f3214.

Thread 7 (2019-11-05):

### ISSUE TITLE
Handling of PRUs in kernel module

### ISSUE THREAD

**Issue by geissdoerfer** [geissdoerfer/shepherd#7]
Currently, the kernel module polls for the PRUs by trying a range of phandles during initialization. This is an ugly workaround and may not work under all circumstances. Instead, the shepherd kernel module should be registered as a platform driver for the PRUs and automatically probed, once the PRUs are detected by the kernel.

**Comment by kugelbit** [comment]
Thanks for filling the Issue.

We can get rid of this "ugly workaround" by writing a platform-driver-kernel-modul. I will go deeper into this in the next few weeks.

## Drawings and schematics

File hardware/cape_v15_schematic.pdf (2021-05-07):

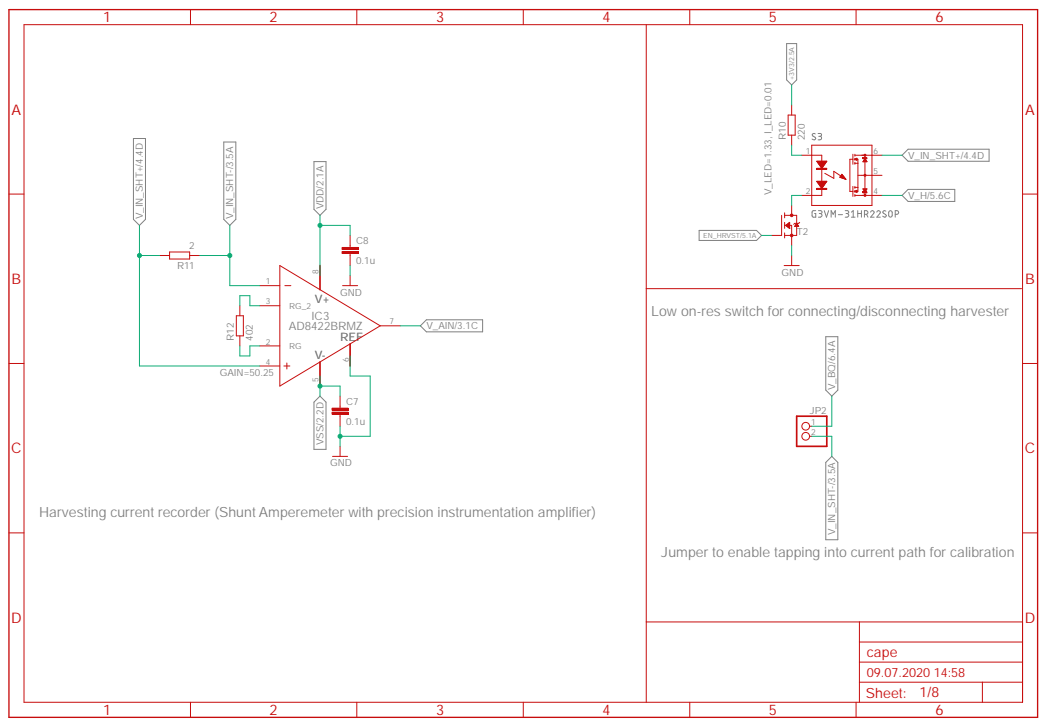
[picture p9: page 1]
V_LED=1.33, I_LED=0.01; GAIN=50.25; REF; GND; AD8422BRMZ; VDD/2.1A; V_IN_SHT+/4.4D; V_AIN/3.1C; VSS/2.2D; V_IN_SHT-/3.5A; V_IN_SHT-/3.5A V_BQ/6.4A; EN_HRVST/5.1A; Sheet:; cape

Low on-res switch for connecting/disconnecting harvester

Harvesting current recorder (Shunt Amperemeter with precision instrumentation amplifier)

Jumper to enable tapping into current path for calibration

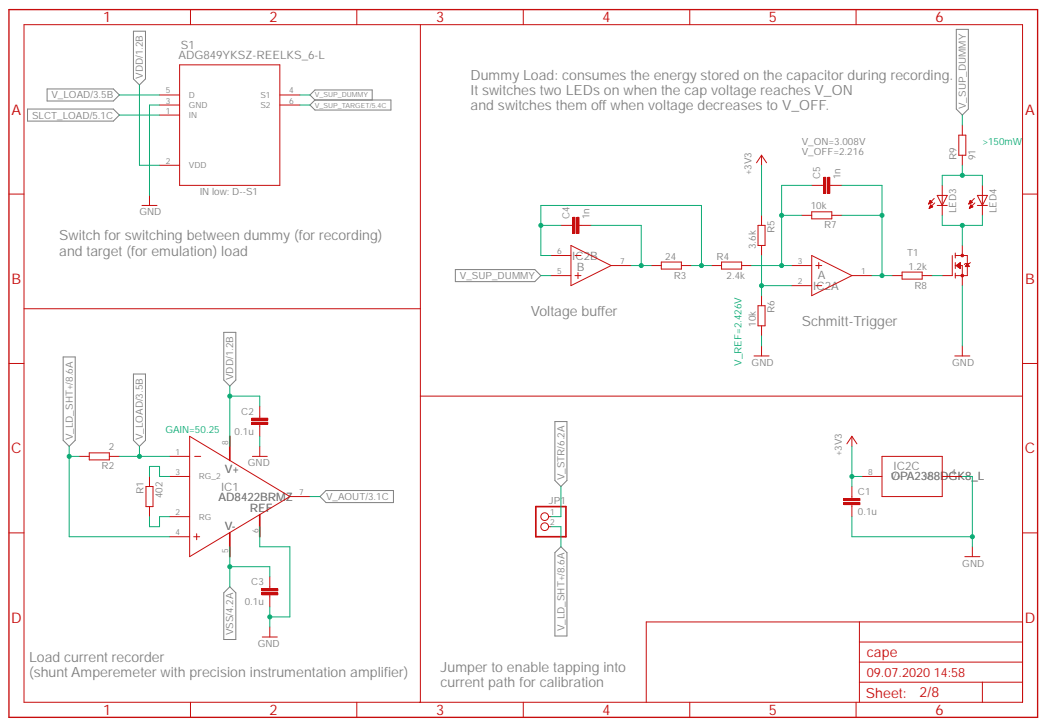
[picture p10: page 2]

Dummy Load: consumes the energy stored on the capacitor during recording.
It switches two LEDs on when the cap voltage reaches V_ON
and switches them off when voltage decreases to V_OFF.

Switch for switching between dummy (for recording)
and target (for emulation) load

current path for calibration

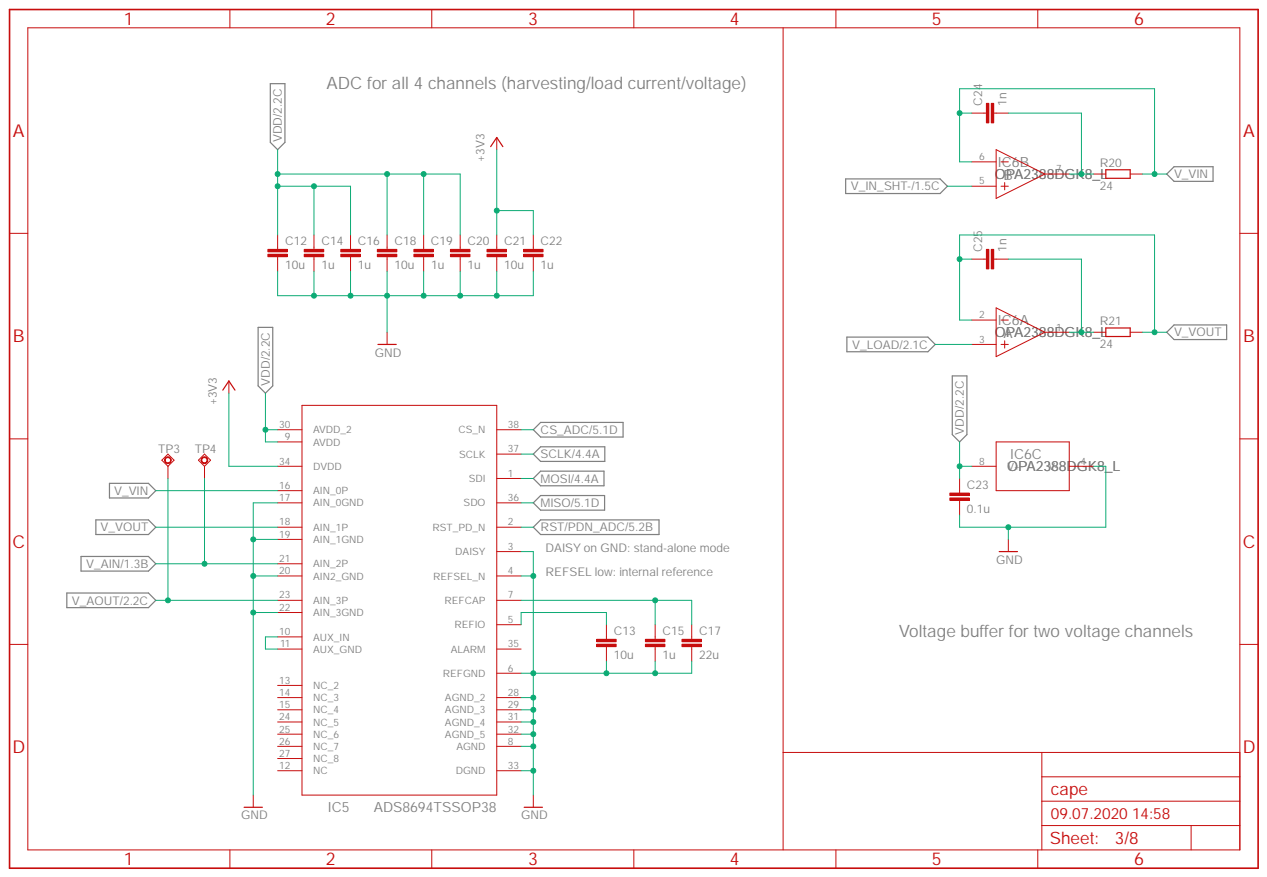
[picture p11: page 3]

ADC for all 4 channels (harvesting/load current/voltage)

DAISY on GND: stand-alone mode
REFSEL low: internal reference

Voltage buffer for two voltage channels

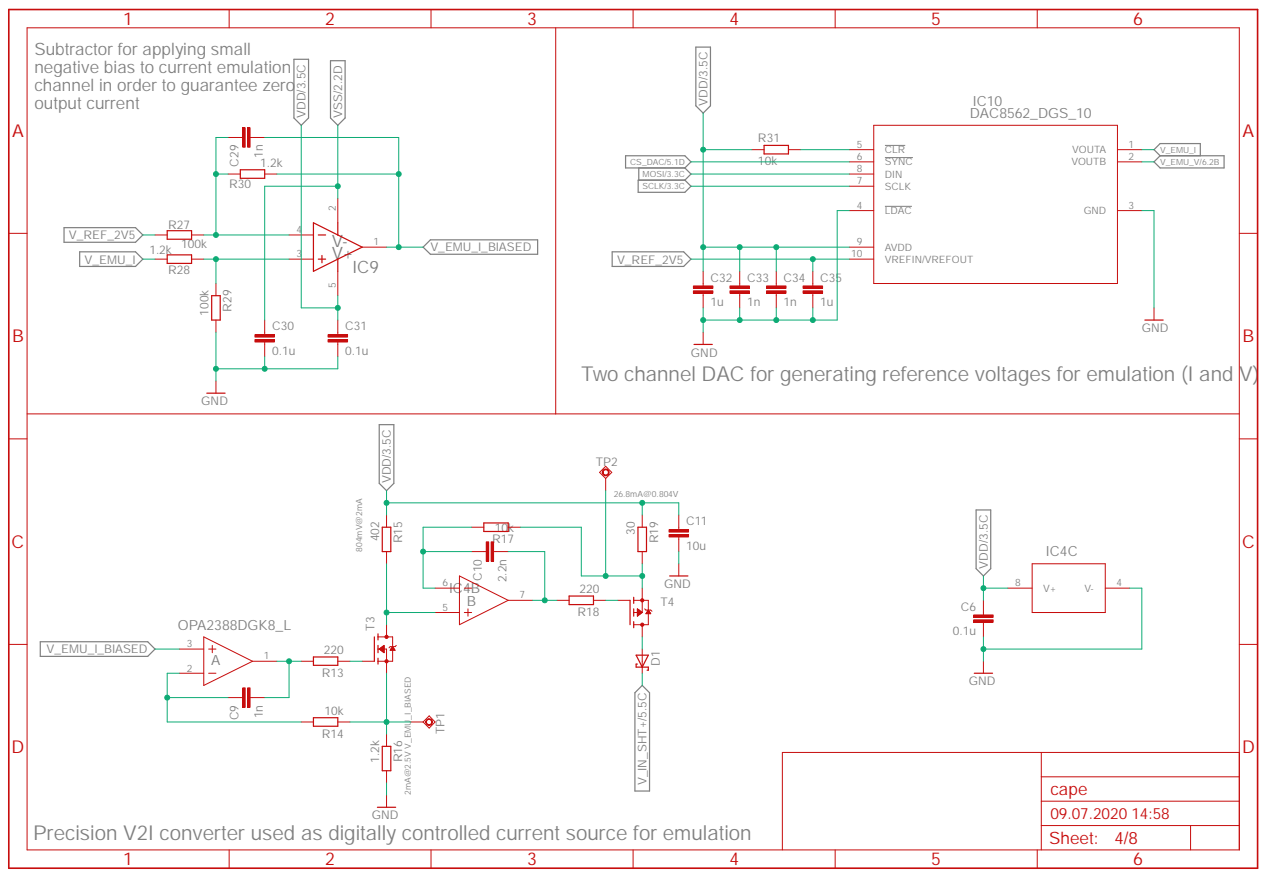
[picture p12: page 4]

Subtractor for applying small
negative bias to current emulation
channel in order to guarantee zero
output current

Two channel DAC for generating reference voltages for emulation (I and V)

Precision V2I converter used as digitally controlled current source for emulation

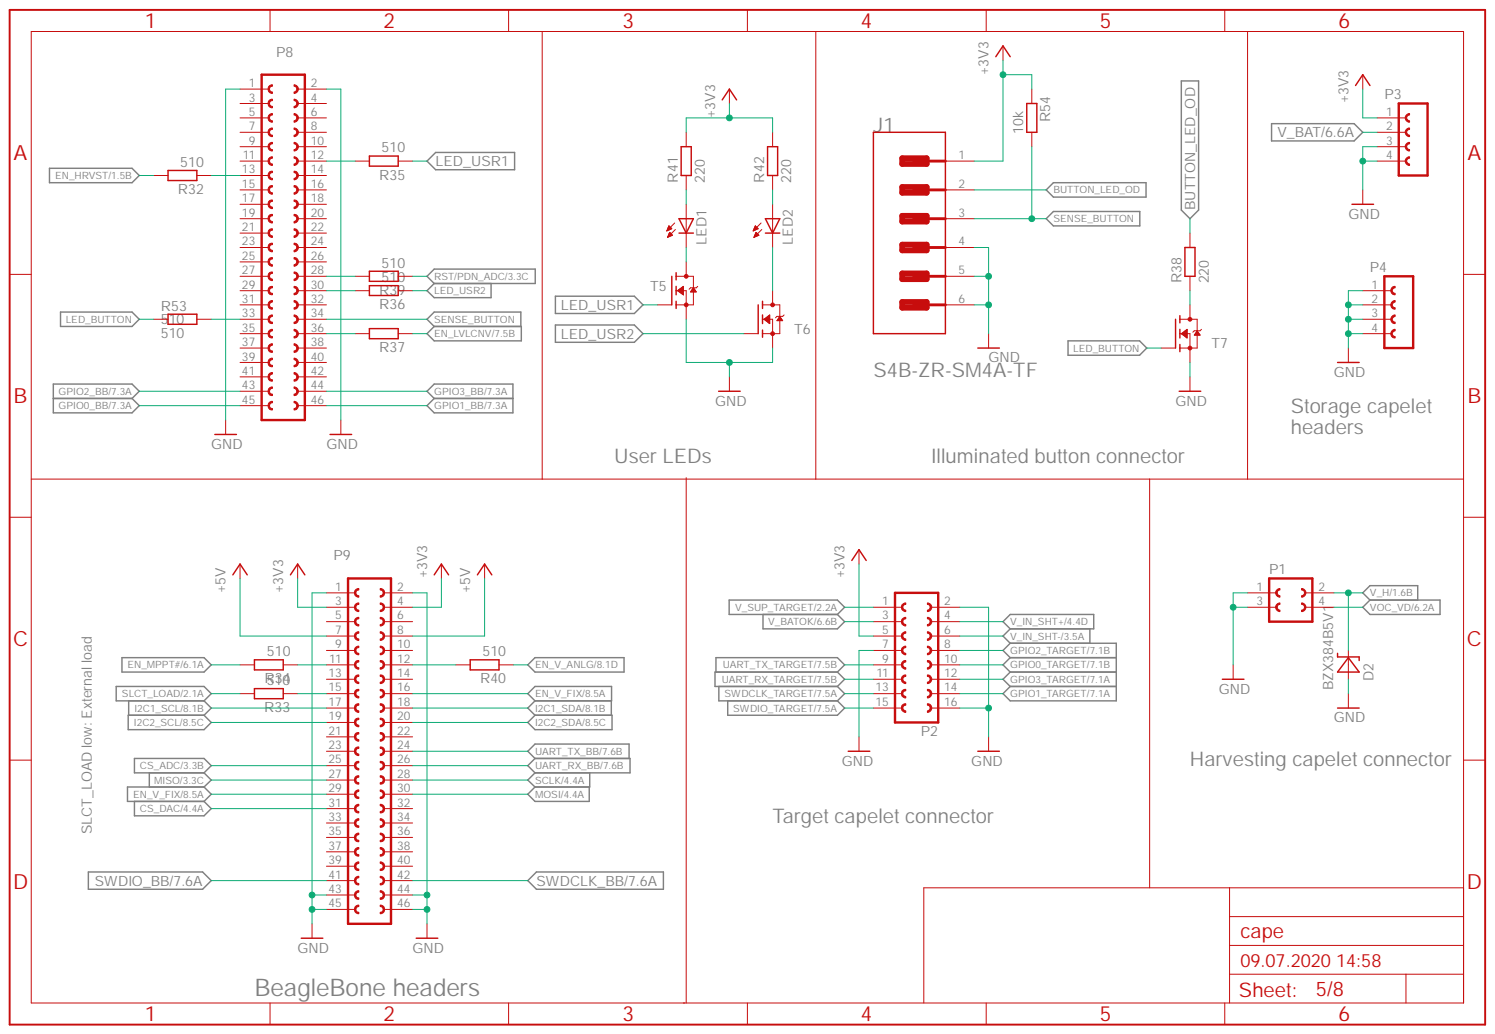
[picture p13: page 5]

LED_BUTTON 510 | 35 | 36

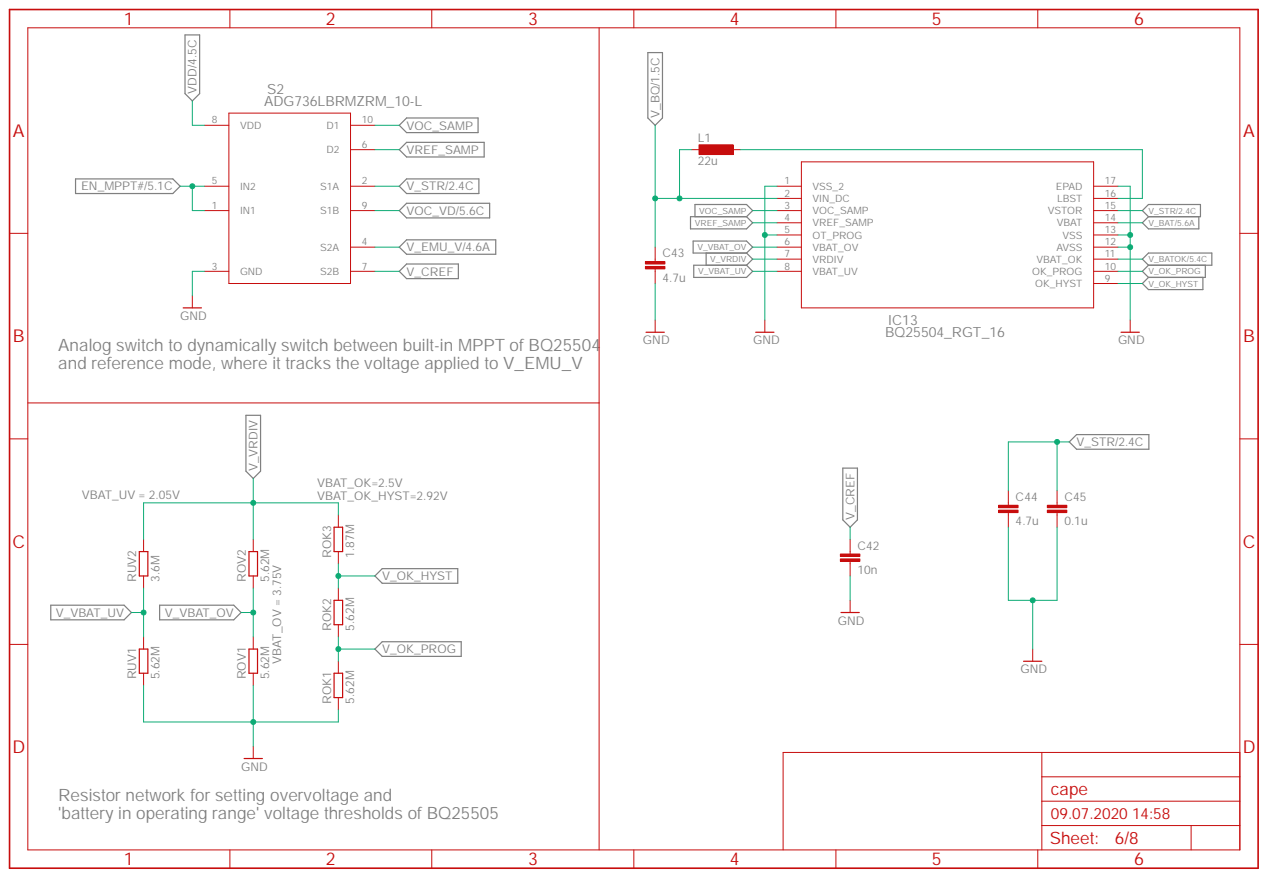
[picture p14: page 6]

Analog switch to dynamically switch between built-in MPPT of BQ25504
and reference mode, where it tracks the voltage applied to V_EMU_V

Resistor network for setting overvoltage and
'battery in operating range' voltage thresholds of BQ25505

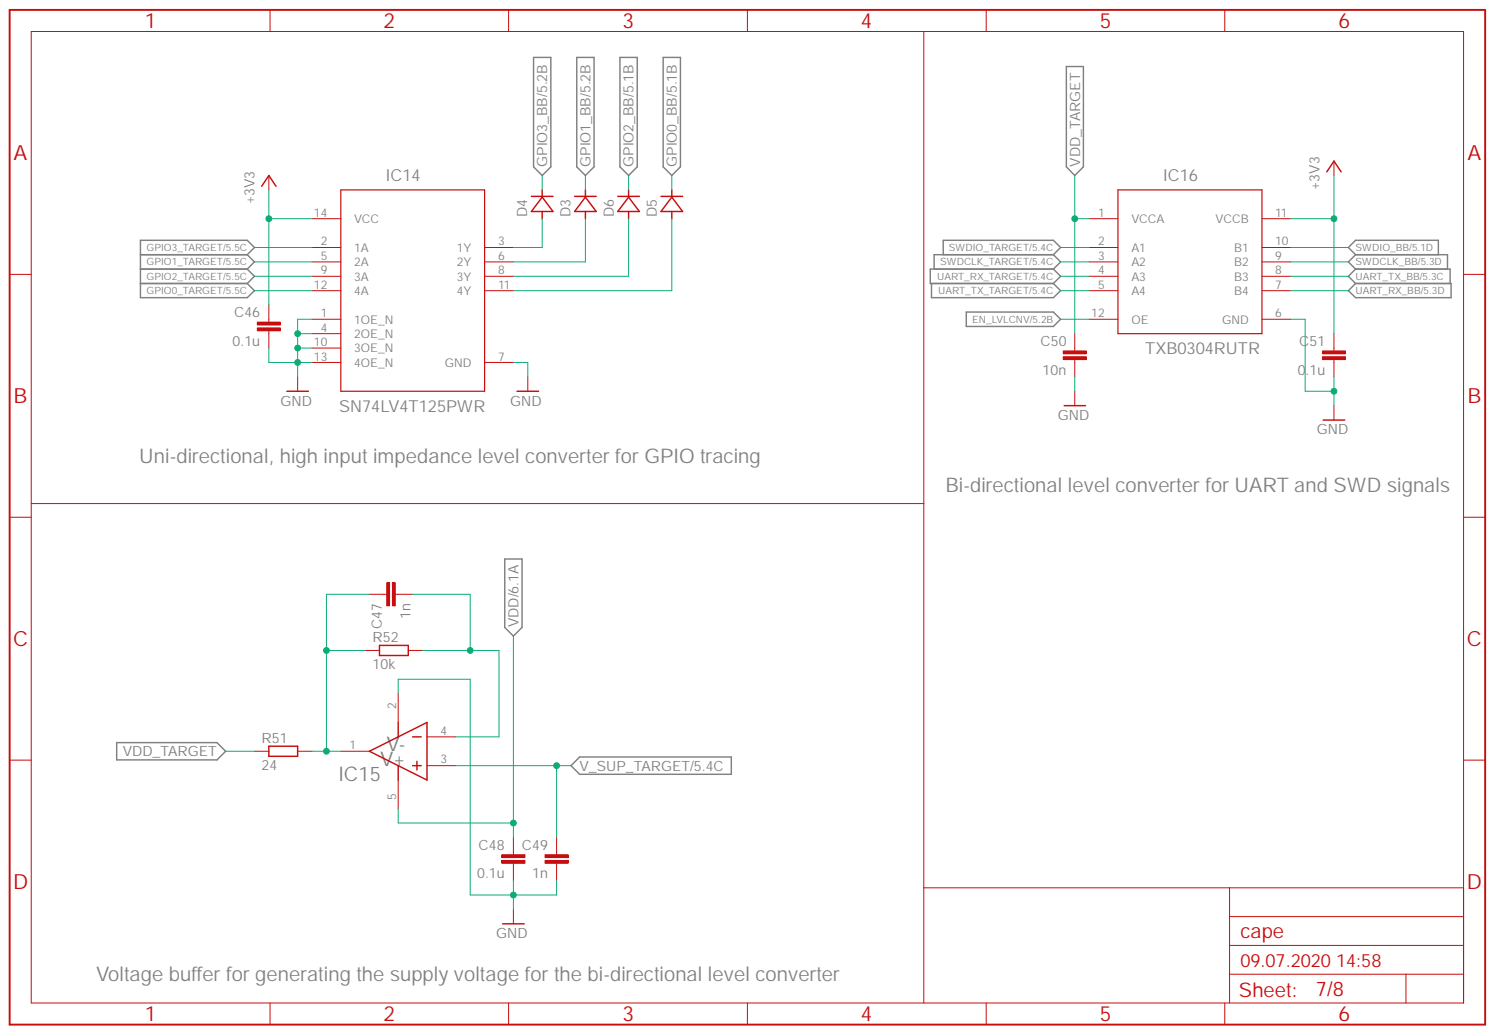
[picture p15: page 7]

Uni-directional, high input impedance level converter for GPIO tracing

Bi-directional level converter for UART and SWD signals

Voltage buffer for generating the supply voltage for the bi-directional level converter

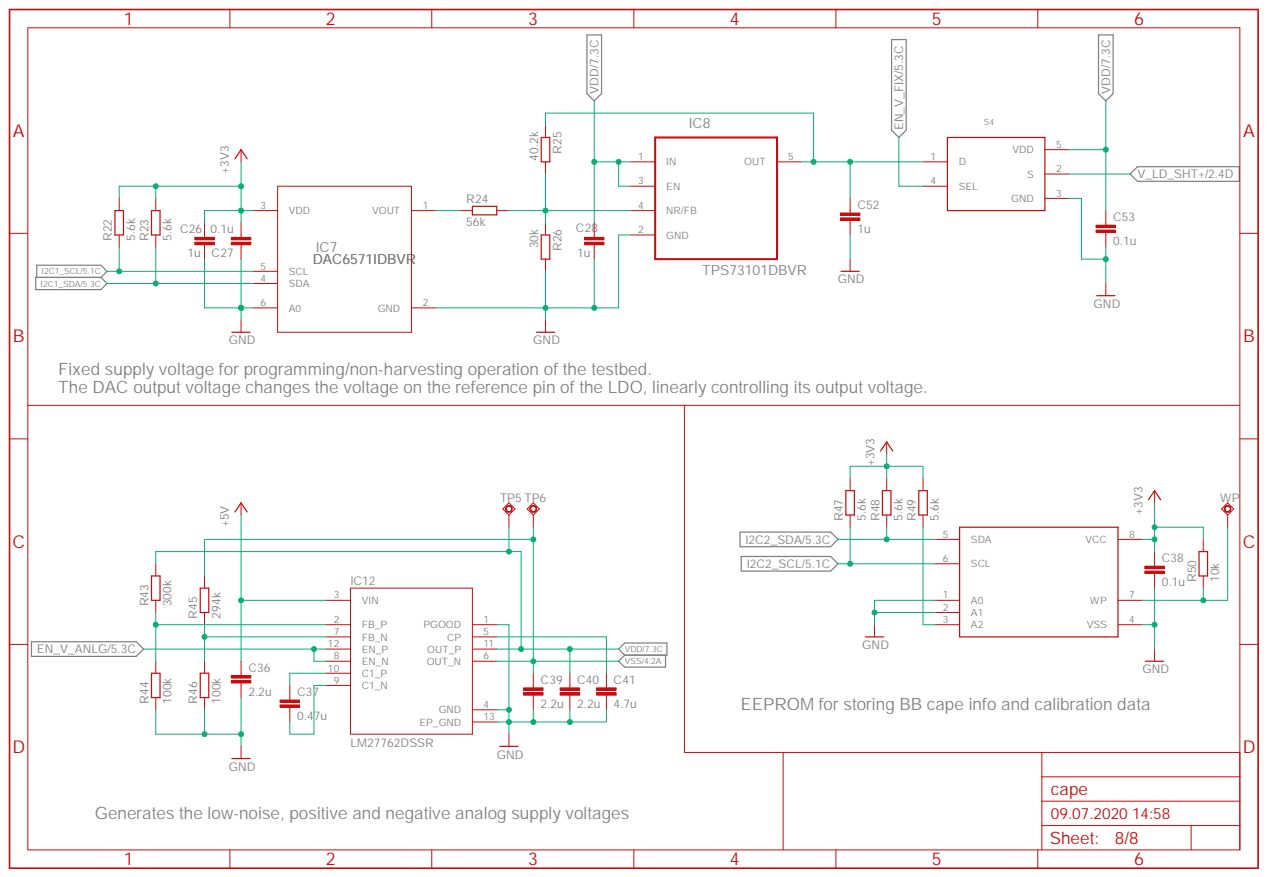
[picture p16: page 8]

SCL 5 SDA 4 A0 6 | C28 | GND 2

Fixed supply voltage for programming/non-harvesting operation of the testbed.
The DAC output voltage changes the voltage on the reference pin of the LDO, linearly controlling its output voltage.

EEPROM for storing BB cape info and calibration data

Generates the low-noise, positive and negative analog supply voltages

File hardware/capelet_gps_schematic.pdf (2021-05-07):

A

A

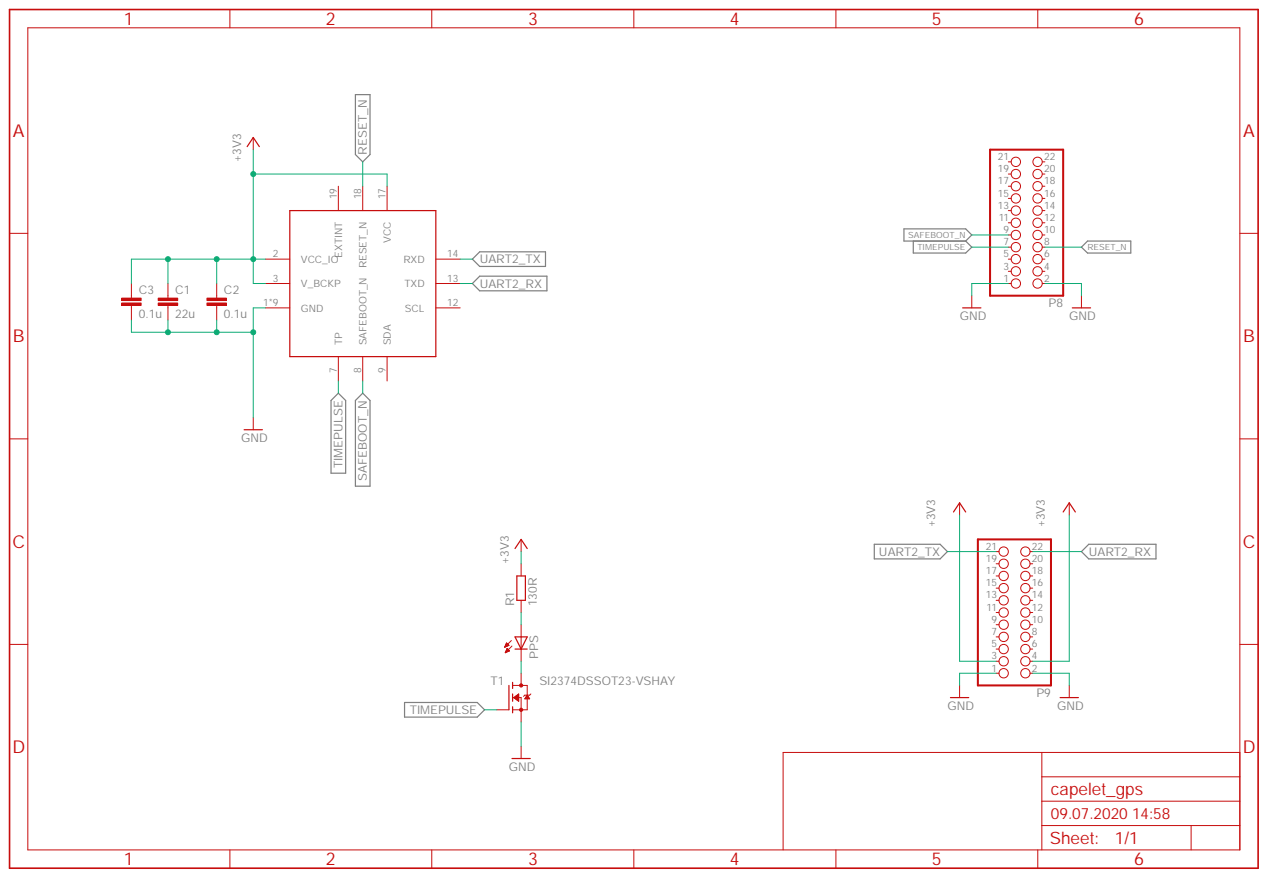
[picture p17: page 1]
+3V3 GND; GNDGND; SI2374DSSOT23-VSHAY; VCC_IO 2; V_BCKP 3; GND 1*9; SAFEBOOT_N; SDA; SCL; TXD; RXD; VCC; RESET_N; EXTINT; PPS; UART2_TX; UART2_RX; TIMEPULSE; Sheet:; capelet_gps

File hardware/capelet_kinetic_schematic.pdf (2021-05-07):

A

A

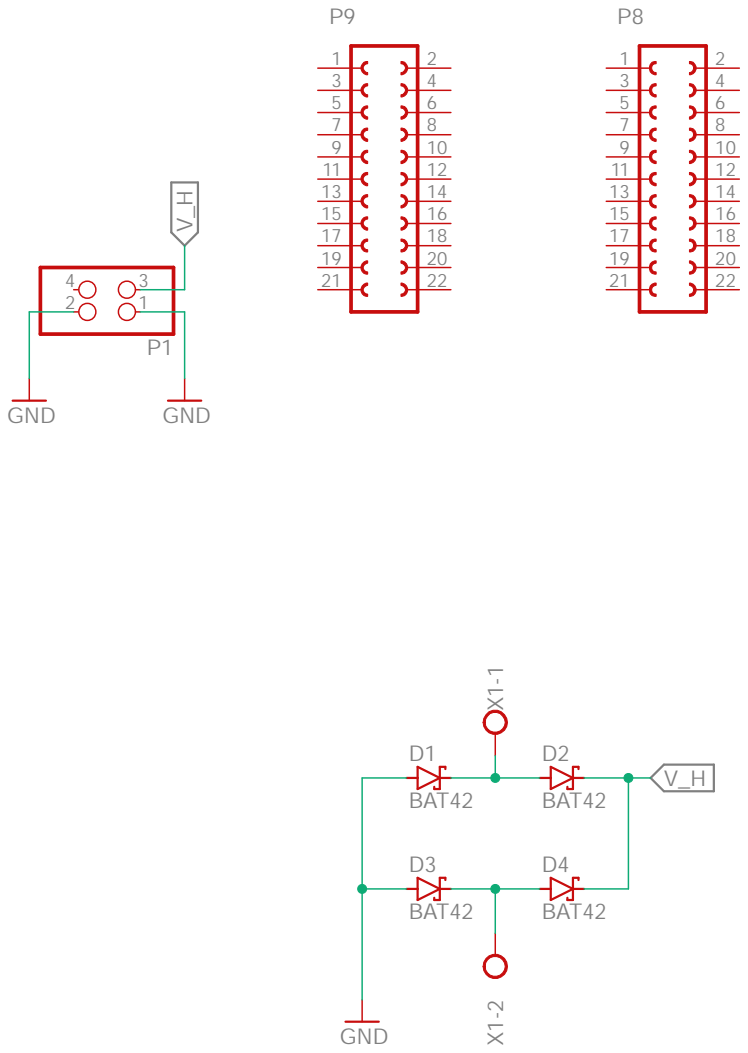
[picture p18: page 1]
BAT42; GND; GNDGND; Sheet:; capelet_kinetic

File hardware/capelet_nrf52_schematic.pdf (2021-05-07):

1

2

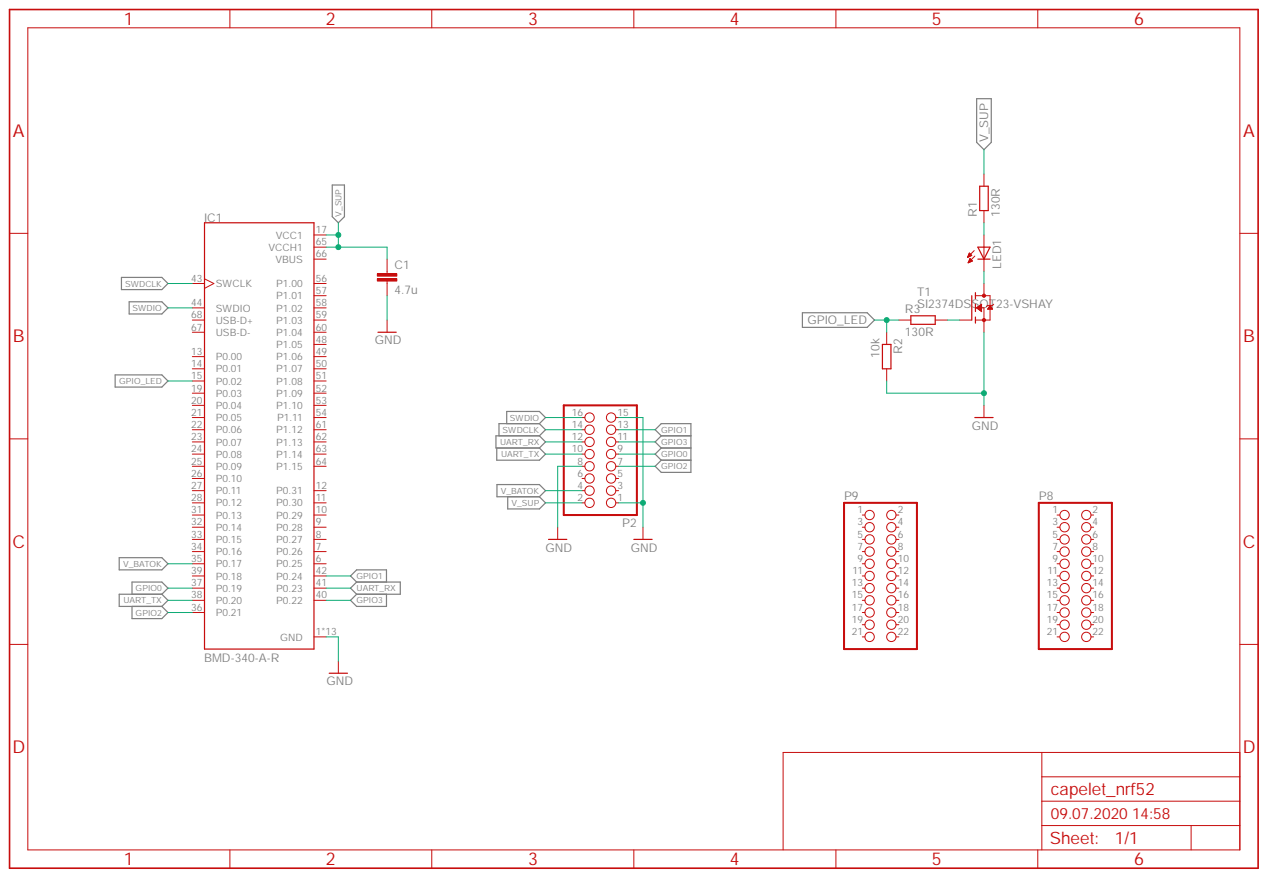
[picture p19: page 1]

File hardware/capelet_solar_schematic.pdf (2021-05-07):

A

A

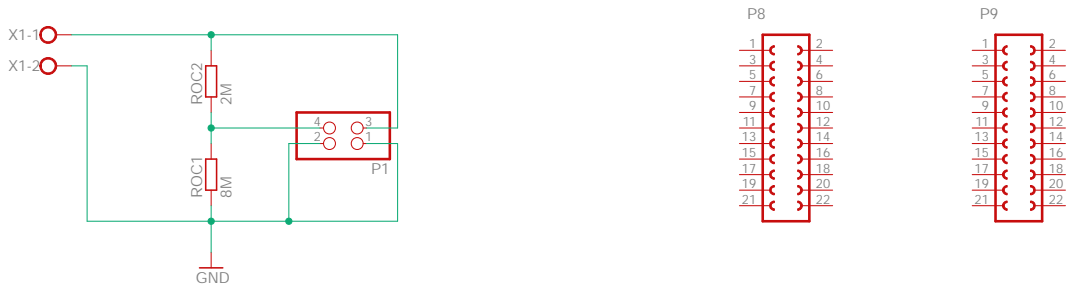
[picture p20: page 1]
GND; ROC2 ROC1; Sheet:; capelet_solar

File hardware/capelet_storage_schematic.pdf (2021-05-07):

GND; Sheet:; capelet_storage

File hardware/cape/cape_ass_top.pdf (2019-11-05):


25.09.19 17:13 f=2.30 /home/kai/eagle/shepherd-hardware/cape/cape.brd



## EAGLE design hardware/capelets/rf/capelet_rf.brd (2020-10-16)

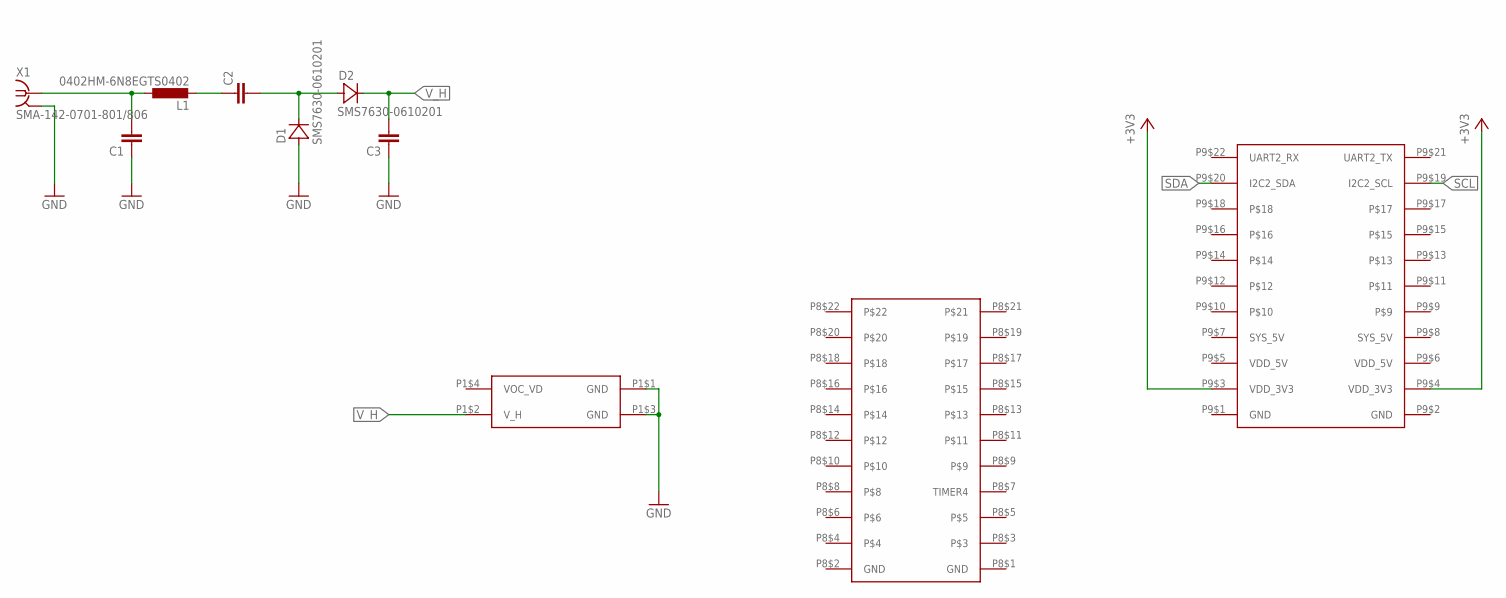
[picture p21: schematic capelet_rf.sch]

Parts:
C1, C2, C3: C_SMD0402; CAPC1005X55
D1, D2: SMS7630-0610201; DIOC0502X27N
L1: 0402HM-6N8EGTS0402; INDC1004X60N
X1: SMA-142-0701-801/806; J502-ND-142-0701-801/806
Y1: SHPRD_CPLT_H

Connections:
+3V3: Y1.P9$3 (VDD_3V3), Y1.P9$4 (VDD_3V3)
GND: C1.1, C3.1, D1.1 (A), X1.G@1 (2), X1.G@2 (2), X1.G@3 (2), X1.G@4 (2), Y1.P1$1 (GND), Y1.P1$3 (GND), Y1.P8$1 (GND), Y1.P8$2 (GND), Y1.P9$1 (GND), Y1.P9$2 (GND)
unnamed: C2.2, D1.2 (C), D2.1 (A)
unnamed: C1.2, L1.1, X1.1
unnamed: C2.1, L1.2
SCL: Y1.P9$19 (I2C2_SCL)
SDA: Y1.P9$20 (I2C2_SDA)
SYS_5V: Y1.P9$7 (SYS_5V), Y1.P9$8 (SYS_5V)
VDD_5V: Y1.P9$5 (VDD_5V), Y1.P9$6 (VDD_5V)
V_H: C3.2, D2.2 (C), Y1.P1$2 (V_H)

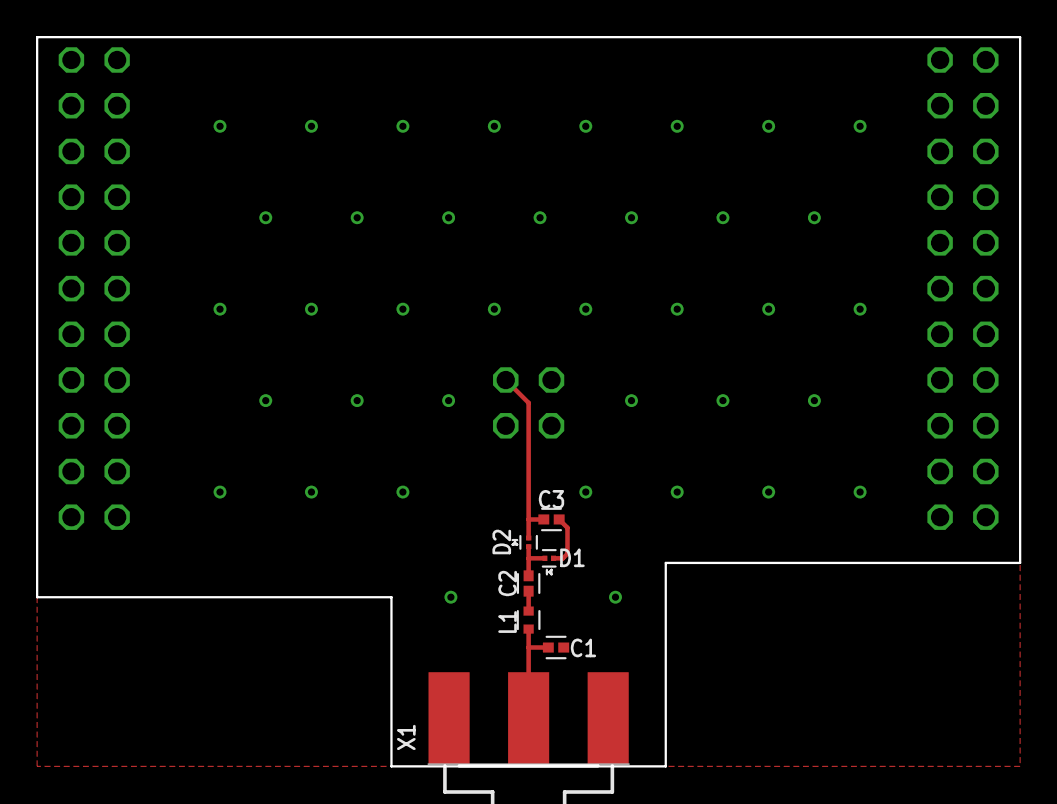
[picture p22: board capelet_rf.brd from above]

Board: 2 copper layers, 54.6 x 40.5 mm, 8 parts (0 on the bottom side), 8 nets.

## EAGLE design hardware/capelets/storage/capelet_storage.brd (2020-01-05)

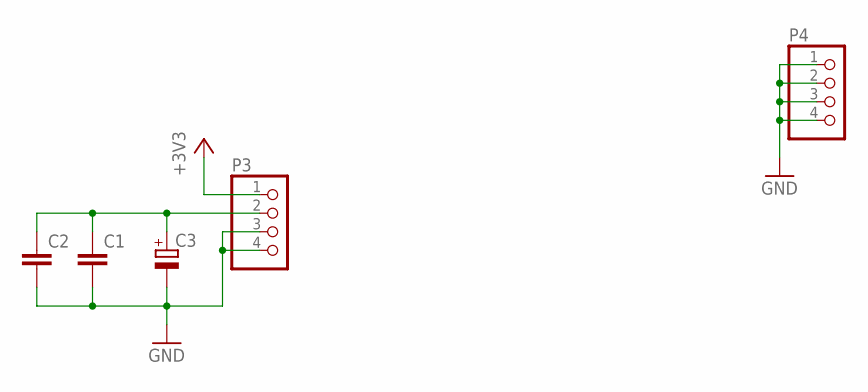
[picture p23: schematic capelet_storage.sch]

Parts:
C1: C_SMD0805; CAPC2012X145
C2: C_SMD1210; CAPC3225X280
C3: CPOL-EUE5-8.5; E5-8,5
P3, P4: PINHD-1X4; 1X04

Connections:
+3V3: P3.1
GND: C1.2, C2.2, C3.-, P3.3, P3.4, P4.1, P4.2, P4.3, P4.4
unnamed: C1.1, C2.1, C3.+, P3.2

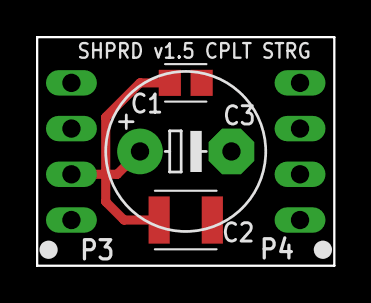
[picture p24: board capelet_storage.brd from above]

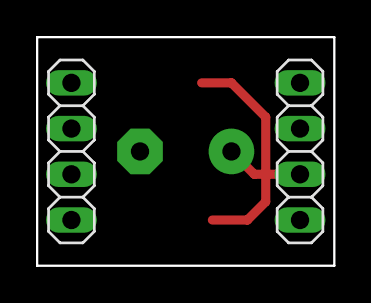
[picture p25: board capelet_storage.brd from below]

Board: 2 copper layers, 16.5 x 12.7 mm, 6 parts (2 on the bottom side), 2 nets.

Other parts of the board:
U$1: SHPRD_CPLT_S

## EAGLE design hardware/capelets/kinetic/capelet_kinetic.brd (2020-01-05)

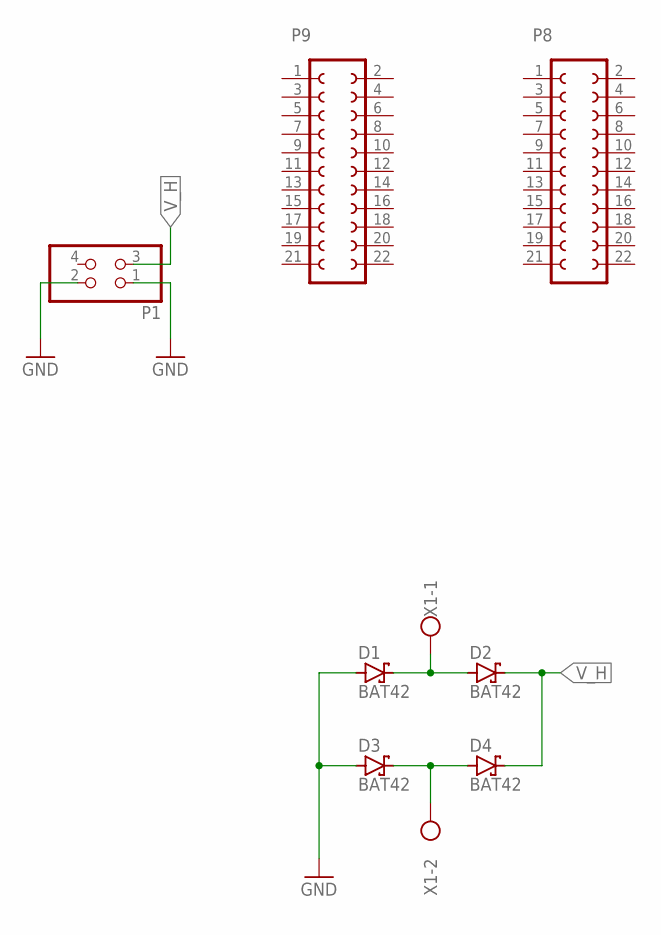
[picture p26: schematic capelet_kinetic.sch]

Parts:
D1, D2, D3, D4: BAT42; DO35-10
P1: PINHD-2X2; 2X02
P8, P9: FE11-2
X1: W237-102

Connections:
GND: D1.A, D3.A, P1.1, P1.2
unnamed: D1.C, D2.A, X1.1
unnamed: D3.C, D4.A, X1.2
V_H: D2.C, D4.C, P1.3

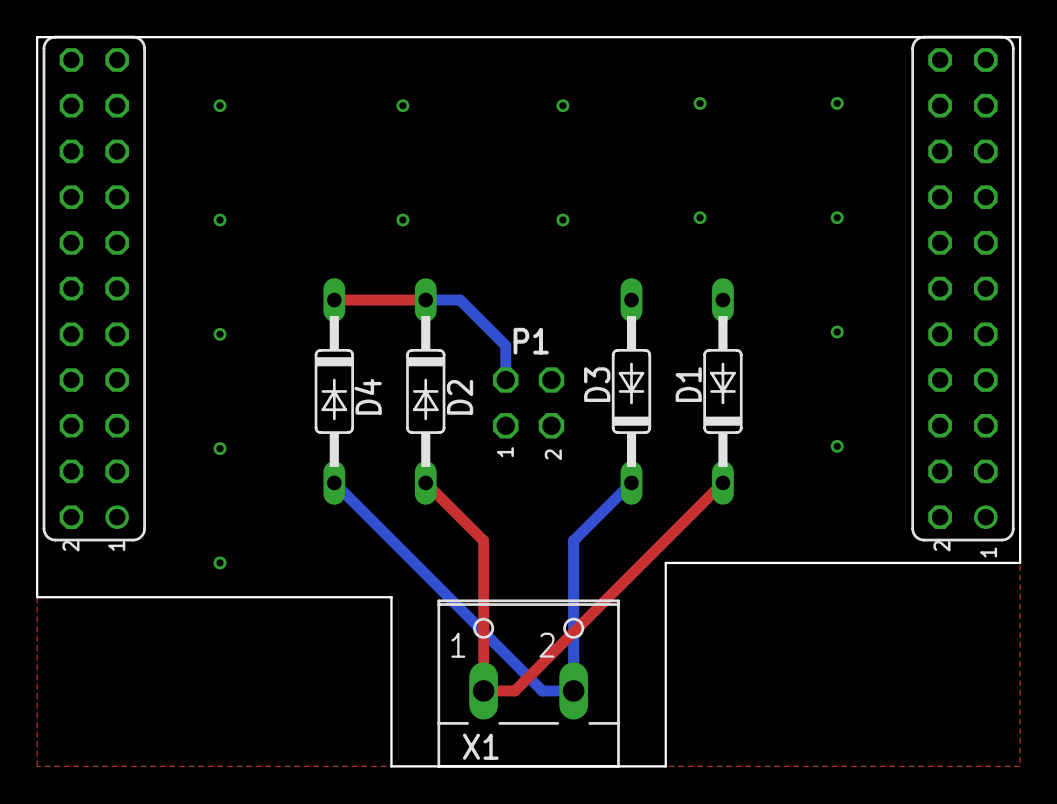
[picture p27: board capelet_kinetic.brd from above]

Board: 2 copper layers, 54.6 x 40.5 mm, 9 parts (1 on the bottom side), 4 nets.

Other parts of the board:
U$1: SHPRD_CPLT_H

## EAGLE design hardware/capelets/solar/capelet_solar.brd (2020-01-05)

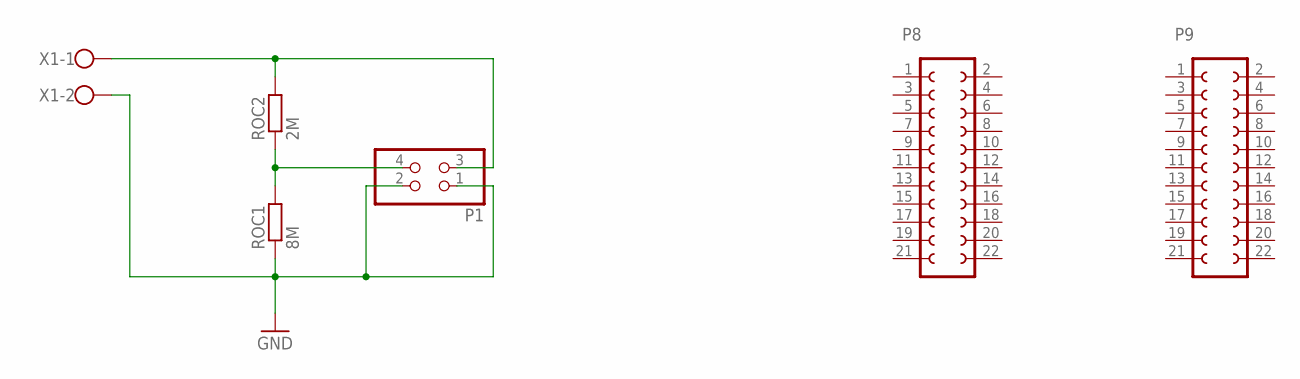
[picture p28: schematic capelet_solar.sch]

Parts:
P1: PINHD-2X2; 2X02
P8, P9: FE11-2
ROC1: 8M; RESC2012X65
ROC2: 2M; RESC2012X65
X1: W237-102

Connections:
GND: P1.1, P1.2, ROC1.1, X1.2
unnamed: P1.3, ROC2.2, X1.1
unnamed: P1.4, ROC1.2, ROC2.1

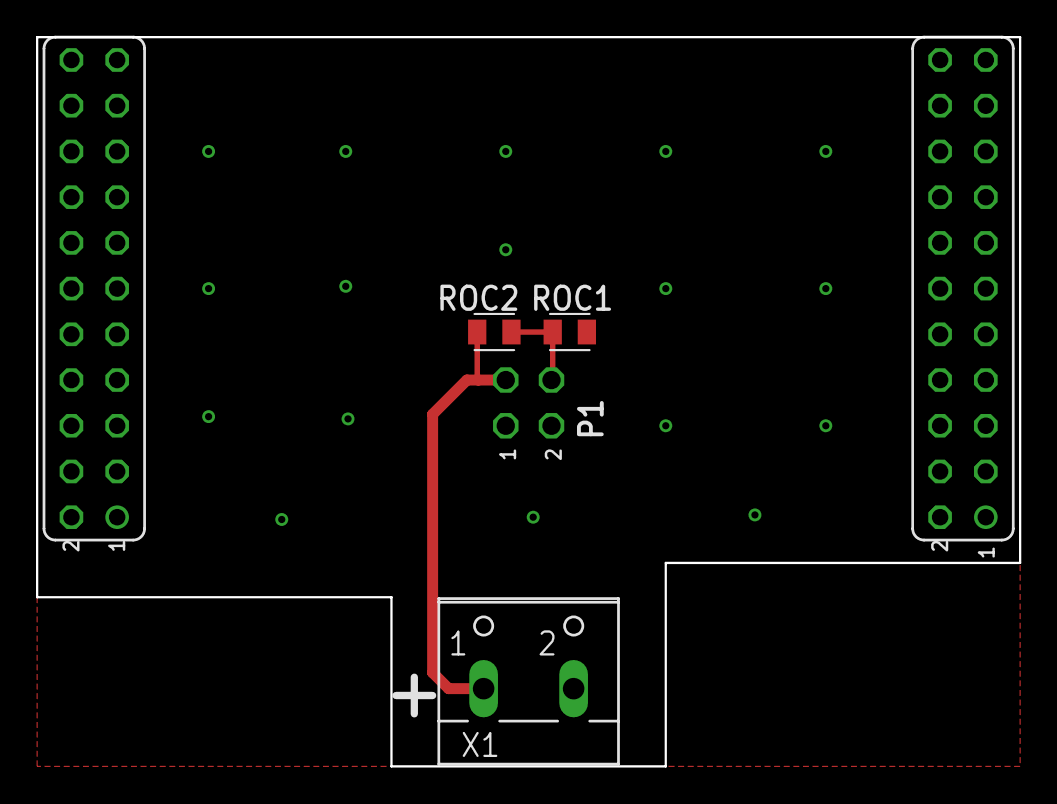
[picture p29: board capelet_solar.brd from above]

Board: 2 copper layers, 54.6 x 40.5 mm, 7 parts (1 on the bottom side), 3 nets.

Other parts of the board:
U$1: SHPRD_CPLT_H

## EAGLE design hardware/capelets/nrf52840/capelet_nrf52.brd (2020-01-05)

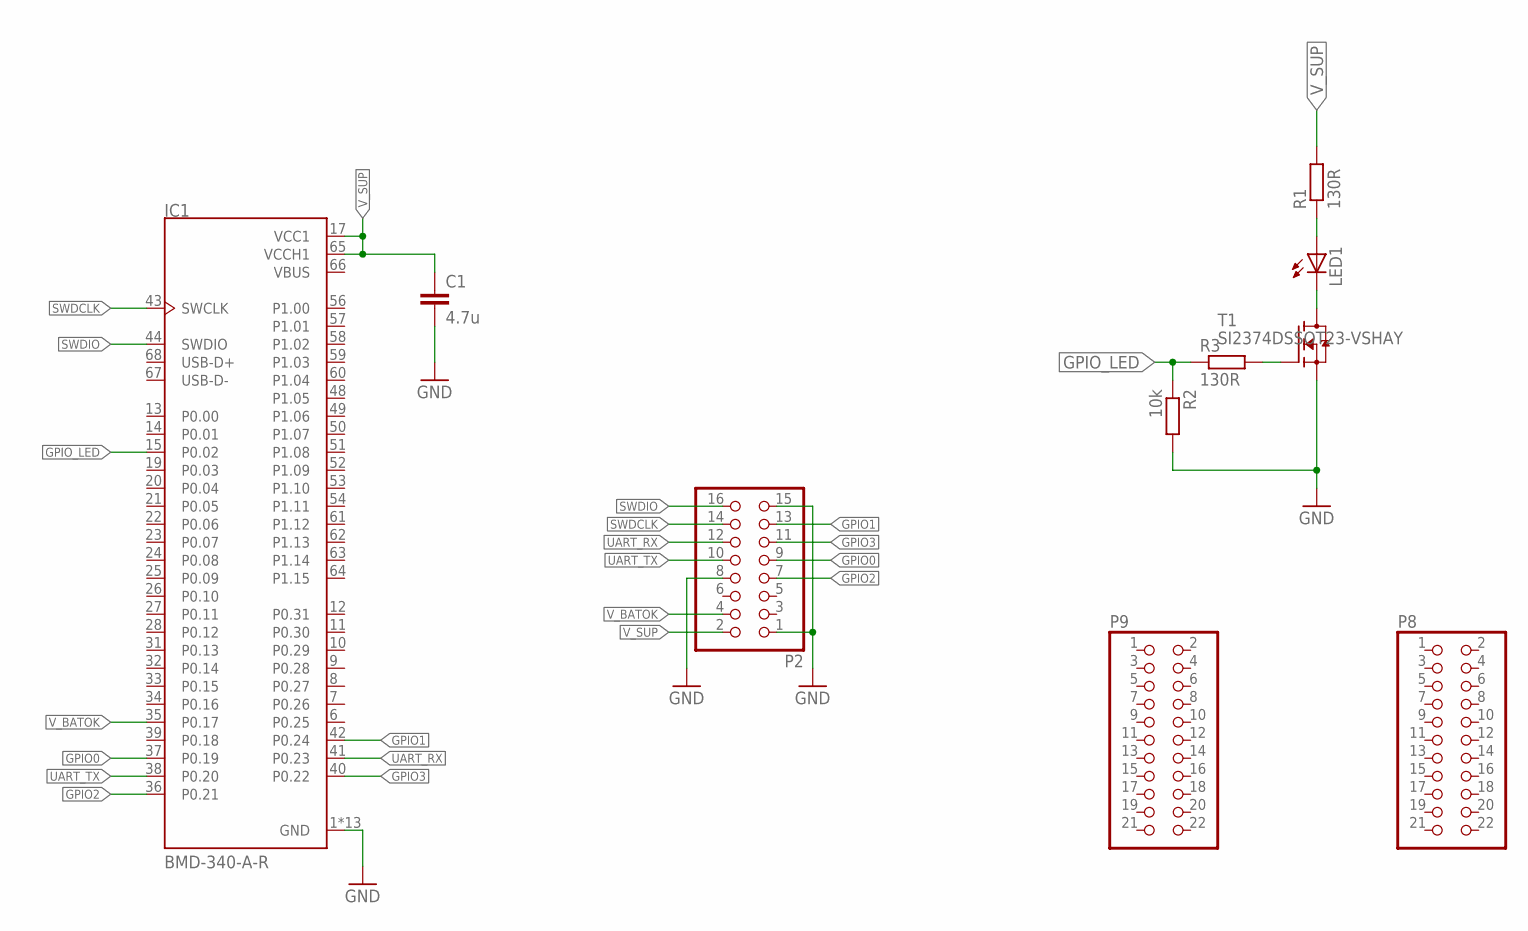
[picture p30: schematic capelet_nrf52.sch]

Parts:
C1: 4.7u; CAPC1608X95
IC1: BMD-340-A-R; RIGADO_BMD-340-A-R
LED1: 598-8130-107FLED_0805; LEDC2012X75
P2: PINHD-2X8; 2X08
P8, P9: PINHD-2X11; 2X11
R1, R3: 130R; RESC2012X65
R2: 10k; RESC2012X65
T1: SI2374DSSOT23-VSHAY; SOT95P237X112-3

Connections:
GND: C1.2, IC1.1 (GND), IC1.2 (GND), IC1.3 (GND), IC1.4 (GND), IC1.5 (GND), IC1.16 (GND), IC1.18 (GND), IC1.29 (GND), IC1.30 (GND), IC1.45 (GND), IC1.46 (GND), IC1.47 (GND), IC1.55 (GND), P2.1, P2.8, P2.15, R2.2, T1.2 (S)
GPIO0: IC1.37 (P0.19), P2.9
GPIO1: IC1.42 (P0.24), P2.13
GPIO2: IC1.36 (P0.21), P2.7
GPIO3: IC1.40 (P0.22), P2.11
GPIO_LED: IC1.15 (P0.02), R2.1, R3.1
unnamed: R3.2, T1.1 (G)
unnamed: LED1.1 (C), T1.3 (D)
unnamed: LED1.2 (A), R1.1
SWDCLK: IC1.43 (SWCLK), P2.14
SWDIO: IC1.44 (SWDIO), P2.16
UART_RX: IC1.41 (P0.23), P2.12
UART_TX: IC1.38 (P0.20), P2.10
VBUS: IC1.66 (VBUS)
V_BATOK: IC1.35 (P0.17), P2.4
V_SUP: C1.1, IC1.17 (VCC1), IC1.65 (VCCH1), P2.2, R1.2

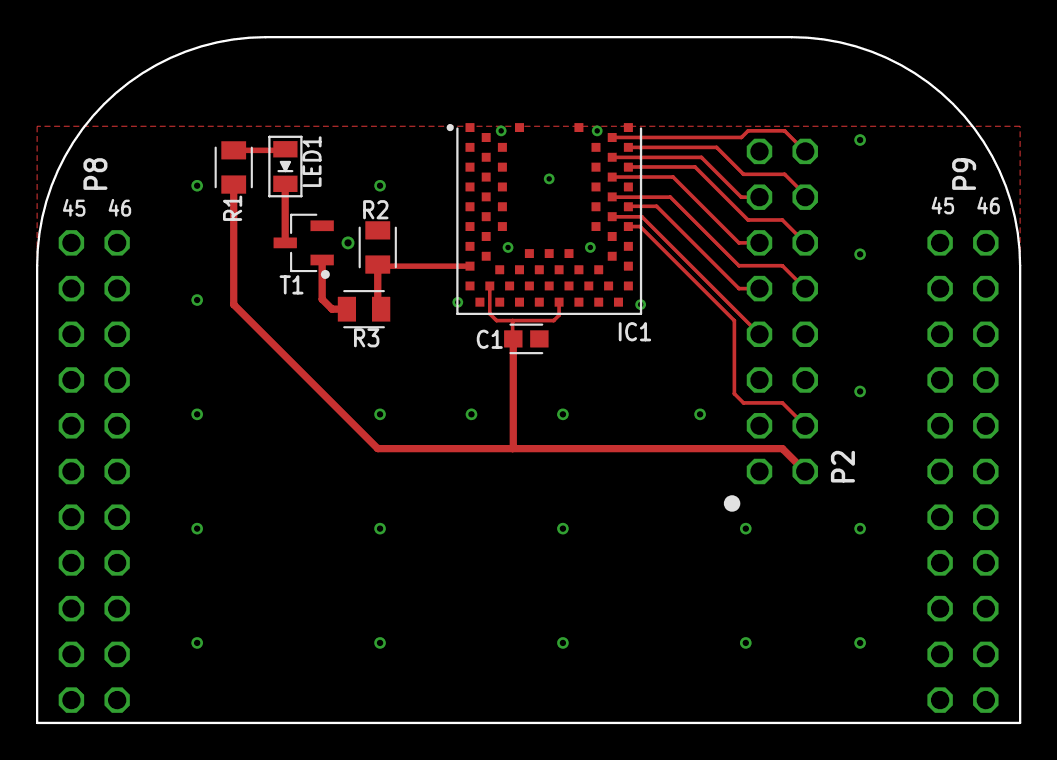
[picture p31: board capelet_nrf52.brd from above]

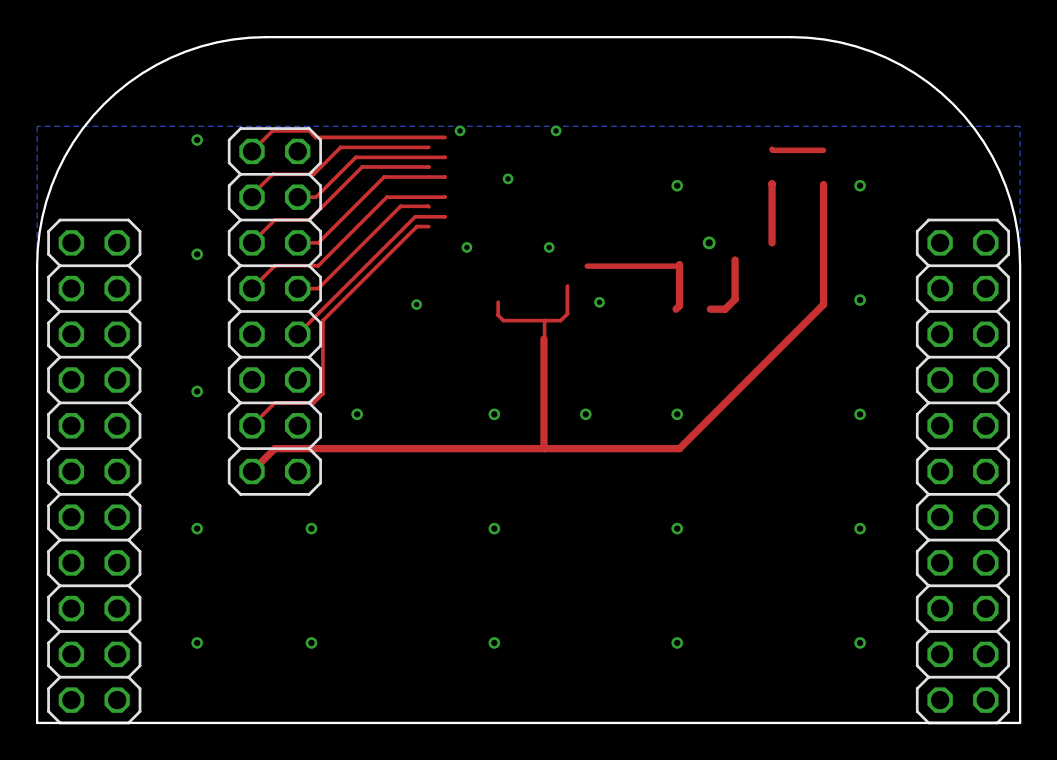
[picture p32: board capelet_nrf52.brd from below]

Board: 2 copper layers, 54.6 x 38.1 mm, 11 parts (3 on the bottom side), 15 nets.

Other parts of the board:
U$3: SHPRD_CPLT_T

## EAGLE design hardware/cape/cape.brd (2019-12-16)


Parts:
C7, C8: 0.1u; CAPC1005X55
IC3: AD8422BRMZ; RM_8-L
JP2: PINHD-1X2; 1X02
R10: 220; RESC1608X55
R11: 2; RESC1608X55
R12: 402; RESC1608X55
S3: G3VM-31HR22SOP; SOP06
T2: SI2374DSSOT23-VSHAY; SOT95P237X112-3

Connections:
+3V3: R10.2; also elsewhere on the board
EN_HRVST: T2.1 (G); also elsewhere on the board
GND: C7.2, C8.2, IC3.6 (REF), T2.2 (S); also elsewhere on the board
unnamed: R10.1, S3.1 (A)
unnamed: IC3.3 (RG_2), R12.2
unnamed: IC3.2 (RG), R12.1
unnamed: S3.2 (K), T2.3 (D)
VDD: C8.1, IC3.8 (V+); also elsewhere on the board
VSS: C7.1, IC3.5 (V-); also elsewhere on the board
V_AIN: IC3.7 (OUT); also elsewhere on the board
V_BQ: JP2.1; also elsewhere on the board
V_H: S3.4 (D2); also elsewhere on the board
V_IN_SHT+: IC3.4 (IN+), R11.2, S3.6 (D1); also elsewhere on the board
V_IN_SHT-: IC3.1 (IN-), JP2.2, R11.1; also elsewhere on the board

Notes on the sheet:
V_LED=1.33, I_LED=0.01
GAIN=50.25
Harvesting current recorder (Shunt Amperemeter with precision instrumentation amplifier)
Low on-res switch for connecting/disconnecting harvester
Jumper to enable tapping into current path for calibration


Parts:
C1, C2, C3: 0.1u; CAPC1005X55
C4, C5: 1n; CAPC1005X55
IC1: AD8422BRMZ; RM_8-L
IC2: OPA2388DGK8_L; DGK8-L
JP1: PINHD-1X2; 1X02
LED3, LED4: 598-8130-107FLED_0805; LEDC2012X75
R1: 402; RESC1608X55
R2: 2; RESC1608X55
R3: 24; RESC1005X40
R4: 2.4k; RESC1005X40
R5: 3.6k; RESC1005X40
R6, R7: 10k; RESC1005X40
R8: 1.2k; RESC1005X40
R9: 91; RESC1608X55
S1: ADG849YKSZ-REELKS_6-L; KS_6-L
T1: SI2374DSSOT23-VSHAY; SOT95P237X112-3

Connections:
+3V3: C1.1, IC2.8 (V+), R5.1; also elsewhere on the board
GND: C1.2, C2.2, C3.2, IC1.6 (REF), IC2.4 (V-), R6.2, S1.3 (GND), T1.2 (S); also elsewhere on the board
unnamed: R8.1, T1.1 (G)
unnamed: LED3.2 (A), LED4.2 (A), R9.1
unnamed: C5.2, IC2.1 (OUT), R7.1, R8.2
unnamed: LED3.1 (C), LED4.1 (C), T1.3 (D)
unnamed: C5.1, IC2.3 (IN+), R4.2, R7.2
unnamed: IC2.2 (IN-), R5.2, R6.1
unnamed: C4.1, IC2.6 (IN-), R3.1, R4.1
unnamed: C4.2, IC2.7 (OUT), R3.2
unnamed: IC1.2 (RG), R1.2
unnamed: IC1.3 (RG_2), R1.1
SLCT_LOAD: S1.1 (IN); also elsewhere on the board
VDD: C2.1, IC1.8 (V+), S1.2 (VDD); also elsewhere on the board
VSS: C3.1, IC1.5 (V-); also elsewhere on the board
V_AOUT: IC1.7 (OUT); also elsewhere on the board
V_LD_SHT+: IC1.4 (IN+), JP1.2, R2.2; also elsewhere on the board
V_LOAD: IC1.1 (IN-), R2.1, S1.5 (D); also elsewhere on the board
V_STR: JP1.1; also elsewhere on the board
V_SUP_DUMMY: IC2.5 (IN+), R9.2, S1.4 (S1)
V_SUP_TARGET: S1.6 (S2); also elsewhere on the board

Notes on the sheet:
IN low: D--S1
GAIN=50.25
V_REF=2.426V
V_ON=3.008V V_OFF=2.216
Dummy Load: consumes the energy stored on the capacitor during recording. It switches two LEDs on when the cap voltage reaches V_ON and switches them off when voltage decreases to V_OFF.
Voltage buffer
Schmitt-Trigger
Switch for switching between dummy (for recording) and target (for emulation) load
Load current recorder (shunt Amperemeter with precision instrumentation amplifier)
Jumper to enable tapping into current path for calibration


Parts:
C12, C13, C18, C21: 10u; CAPC2012X145
C14, C15, C16, C19, C20, C22: 1u; CAPC1608X95
C17: 22u; CAPC3225X280
C23: 0.1u; CAPC1005X55
C24, C25: 1n; CAPC1005X55
IC5: ADS8694TSSOP38; TSSOP38
IC6: OPA2388DGK8_L; DGK8-L
R20, R21: 24; RESC1005X40
TP3, TP4: TPSQTP06R; TP06R

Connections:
+3V3: C21.1, C22.1, IC5.34 (DVDD); also elsewhere on the board
CS_ADC: IC5.38 (CS_N); also elsewhere on the board
GND: C12.2, C13.2, C14.2, C15.2, C16.2, C17.2, C18.2, C19.2, C20.2, C21.2, C22.2, C23.2, IC5.3 (DAISY), IC5.4 (REFSEL_N), IC5.6 (REFGND), IC5.8 (AGND), IC5.17 (AIN_0GND), IC5.19 (AIN_1GND), IC5.20 (AIN2_GND), IC5.22 (AIN_3GND), IC5.28 (AGND_2), IC5.29 (AGND_3), IC5.31 (AGND_4), IC5.32 (AGND_5), IC5.33 (DGND), IC6.4 (V-); also elsewhere on the board
MISO: IC5.36 (SDO); also elsewhere on the board
MOSI: IC5.1 (SDI); also elsewhere on the board
unnamed: C13.1, IC5.5 (REFIO)
unnamed: C15.1, C17.1, IC5.7 (REFCAP)
unnamed: IC5.10 (AUX_IN), IC5.11 (AUX_GND)
unnamed: C25.2, IC6.1 (OUT), R21.1
unnamed: C24.2, IC6.7 (OUT), R20.1
RST/PDN_ADC: IC5.2 (RST_PD_N); also elsewhere on the board
SCLK: IC5.37 (SCLK); also elsewhere on the board
VDD: C12.1, C14.1, C16.1, C18.1, C19.1, C20.1, C23.1, IC5.9 (AVDD), IC5.30 (AVDD_2), IC6.8 (V+); also elsewhere on the board
V_AIN: IC5.21 (AIN_2P), TP4.TP; also elsewhere on the board
V_AOUT: IC5.23 (AIN_3P), TP3.TP; also elsewhere on the board
V_IN_SHT-: IC6.5 (IN+); also elsewhere on the board
V_LOAD: IC6.3 (IN+); also elsewhere on the board
V_VIN: C24.1, IC5.16 (AIN_0P), IC6.6 (IN-), R20.2
V_VOUT: C25.1, IC5.18 (AIN_1P), IC6.2 (IN-), R21.2

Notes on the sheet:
REFSEL low: internal reference
DAISY on GND: stand-alone mode
ADC for all 4 channels (harvesting/load current/voltage)
Voltage buffer for two voltage channels


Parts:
C6, C30, C31: 0.1u; CAPC1005X55
C9, C29, C33, C34: 1n; CAPC1005X55
C10: 2.2n; CAPC1005X55
C11: 10u; CAPC2012X145
C32, C35: 1u; CAPC1608X95
D1: BAT43WS-HE3SOD-323; SOD2513X110
IC4: OPA2388DGK8_L; DGK8-L
IC9: LMP7701MF; DBV5-L
IC10: DAC8562_DGS_10; DGS10
R13, R18: 220; RESC1608X55
R14, R17, R31: 10k; RESC1005X40
R15: 402; RESC1608X55
R16, R28, R30: 1.2k; RESC1005X40
R19: 30; RESC1005X40
R27, R29: 100k; RESC1005X40
T3: SI2374DSSOT23-VSHAY; SOT95P237X112-3
T4: SI2307SOT23-VSHAY; SOT95P237X112-3
TP1, TP2: TPSQTP06R; TP06R

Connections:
CS_DAC: IC10.6 (!SYNC); also elsewhere on the board
GND: C6.2, C11.2, C30.2, C31.2, C32.2, C33.2, C34.2, C35.2, IC4.4 (V-), IC10.3 (GND), IC10.4 (!LDAC), R16.2, R29.2; also elsewhere on the board
MOSI: IC10.8 (DIN); also elsewhere on the board
unnamed: C9.2, IC4.1 (OUT), R13.2
unnamed: C9.1, IC4.2 (IN-), R14.2
unnamed: IC10.5 (!CLR), R31.2
unnamed: D1.2 (A), T4.3 (D)
unnamed: C29.1, IC9.4 (IN-), R27.1, R30.2
unnamed: IC9.3 (IN+), R28.1, R29.1
unnamed: R13.1, T3.1 (G)
unnamed: R14.1, R16.1, T3.2 (S), TP1.TP
unnamed: IC4.5 (IN+), R15.2, T3.3 (D)
unnamed: C10.1, IC4.6 (IN-), R17.2
unnamed: C10.2, IC4.7 (OUT), R18.2
unnamed: R18.1, T4.1 (G)
unnamed: R17.1, R19.2, T4.2 (S), TP2.TP
SCLK: IC10.7 (SCLK); also elsewhere on the board
VDD: C6.1, C11.1, C31.1, C32.1, C33.1, C34.1, IC4.8 (V+), IC9.5 (V+), IC10.9 (AVDD), R15.1, R19.1, R31.1; also elsewhere on the board
VSS: C30.1, IC9.2 (V-); also elsewhere on the board
V_EMU_I: IC10.1 (VOUTA), R28.2
V_EMU_I_BIASED: C29.2, IC4.3 (IN+), IC9.1 (OUT), R30.1
V_EMU_V: IC10.2 (VOUTB); also elsewhere on the board
V_IN_SHT+: D1.1 (C); also elsewhere on the board
V_REF_2V5: C35.1, IC10.10 (VREFIN/VREFOUT), R27.2

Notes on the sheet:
Two channel DAC for generating reference voltages for emulation (I and V)
Subtractor for applying small negative bias to current emulation channel in order to guarantee zero output current
2mA@2.5V V_EMU_I_BIASED
804mV@2mA
26.8mA@0.804V
Precision V2I converter used as digitally controlled current source for emulation

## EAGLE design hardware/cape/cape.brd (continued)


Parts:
D2: BZX384B5V1; SOD2513X110
J1: JST_S4B-ZR-SM4A-TFJST_S4B-ZR-SM4A-TF_0_0; JST_S4B-ZR-SM4A-TF_0
LED1, LED2: 598-8130-107FLED_0805; LEDC2012X75
P1: FE02-2
P2: FE08-2
P3, P4: FE04-1
P8, P9: FE23-2
R32, R33, R34, R35, R36, R37, R39, R40, R53: 510; RESC1005X40
R38, R41, R42: 220; RESC1608X55
R54: 10k; RESC1005X40
T5, T6, T7: SI2374DSSOT23-VSHAY; SOT95P237X112-3

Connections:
+3V3: J1.1, P2.5, P3.1, P9.3, P9.4, R41.2, R42.2, R54.1; also elsewhere on the board
+5V: P9.7, P9.8; also elsewhere on the board
BUTTON_LED_OD: J1.2, R38.2
CS_ADC: P9.25; also elsewhere on the board
CS_DAC: P9.31; also elsewhere on the board
EN_HRVST: R32.2; also elsewhere on the board
EN_LVLCNV: R37.1; also elsewhere on the board
EN_MPPT#: R34.2; also elsewhere on the board
EN_V_ANLG: R40.1; also elsewhere on the board
EN_V_FIX: P9.16, P9.29; also elsewhere on the board
GND: D2.2 (A), J1.4, J1.5 (MNT_1), J1.6 (MNT_2), P1.1, P1.3, P2.2, P2.7, P2.16, P3.3, P3.4, P4.1, P4.2, P4.3, P4.4, P8.1, P8.2, P9.1, P9.2, P9.43, P9.44, P9.45, P9.46, T5.2 (S), T6.2 (S), T7.2 (S); also elsewhere on the board
GPIO0_BB: P8.45; also elsewhere on the board
GPIO0_TARGET: P2.10; also elsewhere on the board
GPIO1_BB: P8.46; also elsewhere on the board
GPIO1_TARGET: P2.14; also elsewhere on the board
GPIO2_BB: P8.43; also elsewhere on the board
GPIO2_TARGET: P2.8; also elsewhere on the board
GPIO3_BB: P8.44; also elsewhere on the board
GPIO3_TARGET: P2.12; also elsewhere on the board
I2C1_SCL: P9.17; also elsewhere on the board
I2C1_SDA: P9.18; also elsewhere on the board
I2C2_SCL: P9.19; also elsewhere on the board
I2C2_SDA: P9.20; also elsewhere on the board
LED_BUTTON: R53.1, T7.1 (G)
LED_USR1: R35.1, T5.1 (G)
LED_USR2: R36.1, T6.1 (G)
MISO: P9.27; also elsewhere on the board
MOSI: P9.30; also elsewhere on the board
unnamed: LED1.1 (C), T5.3 (D)
unnamed: P8.13, R32.1
unnamed: P9.15, R33.1
unnamed: P8.28, R39.2
unnamed: P8.33, R53.2
unnamed: P8.36, R37.2
unnamed: LED1.2 (A), R41.1
unnamed: P8.12, R35.2
unnamed: LED2.1 (C), T6.3 (D)
unnamed: LED2.2 (A), R42.1
unnamed: P9.11, R34.1
unnamed: P8.30, R36.2
unnamed: R38.1, T7.3 (D)
unnamed: P9.12, R40.2
RST/PDN_ADC: R39.1; also elsewhere on the board
SCLK: P9.28; also elsewhere on the board
SENSE_BUTTON: J1.3, P8.34, R54.2
SLCT_LOAD: R33.2; also elsewhere on the board
SWDCLK_BB: P9.42; also elsewhere on the board
SWDCLK_TARGET: P2.13; also elsewhere on the board
SWDIO_BB: P9.41; also elsewhere on the board
SWDIO_TARGET: P2.15; also elsewhere on the board
UART_RX_BB: P9.26; also elsewhere on the board
UART_RX_TARGET: P2.11; also elsewhere on the board
UART_TX_BB: P9.24; also elsewhere on the board
UART_TX_TARGET: P2.9; also elsewhere on the board
VOC_VD: P1.4; also elsewhere on the board
V_BAT: P3.2; also elsewhere on the board
V_BATOK: P2.3; also elsewhere on the board
V_H: D2.1 (C), P1.2; also elsewhere on the board
V_IN_SHT+: P2.4; also elsewhere on the board
V_IN_SHT-: P2.6; also elsewhere on the board
V_SUP_TARGET: P2.1; also elsewhere on the board

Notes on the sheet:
SLCT_LOAD low: External load
Storage capelet headers
User LEDs
Harvesting capelet connector
Target capelet connector
BeagleBone headers
Illuminated button connector


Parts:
C42: 10n; CAPC1005X55
C43, C44: 4.7u; CAPC2012X145
C45: 0.1u; CAPC1005X55
IC13: BQ25504_RGT_16; RGT16_1P7X1P7
L1: 22u; L3225P
ROK1, ROK2: 5.62M; RESC1608X55
ROK3: 1.87M; RESC1608X55
ROV1, ROV2: 5.62M; RESC1608X55
RUV1: 5.62M; RESC1608X55
RUV2: 3.6M; RESC1608X55
S2: ADG736LBRMZRM_10-L; RM_10-L

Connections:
EN_MPPT#: S2.1 (IN1), S2.5 (IN2); also elsewhere on the board
GND: C42.2, C43.2, C44.2, C45.2, IC13.1 (VSS_2), IC13.5 (OT_PROG), IC13.12 (AVSS), IC13.13 (VSS), IC13.17 (EPAD), ROK1.1, ROV1.1, RUV1.1, S2.3 (GND); also elsewhere on the board
unnamed: IC13.16 (LBST), L1.1
VDD: S2.8 (VDD); also elsewhere on the board
VOC_SAMP: IC13.3 (VOC_SAMP), S2.10 (D1)
VOC_VD: S2.9 (S1B); also elsewhere on the board
VREF_SAMP: IC13.4 (VREF_SAMP), S2.6 (D2)
V_BAT: IC13.14 (VBAT); also elsewhere on the board
V_BATOK: IC13.11 (VBAT_OK); also elsewhere on the board
V_BQ: C43.1, IC13.2 (VIN_DC), L1.2; also elsewhere on the board
V_CREF: C42.1, S2.7 (S2B)
V_EMU_V: S2.4 (S2A); also elsewhere on the board
V_OK_HYST: IC13.9 (OK_HYST), ROK2.2, ROK3.1
V_OK_PROG: IC13.10 (OK_PROG), ROK1.2, ROK2.1
V_STR: C44.1, C45.1, IC13.15 (VSTOR), S2.2 (S1A); also elsewhere on the board
V_VBAT_OV: IC13.6 (VBAT_OV), ROV1.2, ROV2.1
V_VBAT_UV: IC13.8 (VBAT_UV), RUV1.2, RUV2.1
V_VRDIV: IC13.7 (VRDIV), ROK3.2, ROV2.2, RUV2.2

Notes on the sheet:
VBAT_OK=2.5V VBAT_OK_HYST=2.92V
VBAT_OV = 3.75V
Analog switch to dynamically switch between built-in MPPT of BQ25504 and reference mode, where it tracks the voltage applied to V_EMU_V
Resistor network for setting overvoltage and 'battery in operating range' voltage thresholds of BQ25505
VBAT_UV = 2.05V


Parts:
C46, C48, C51: 0.1u; CAPC1005X55
C47, C49: 1n; CAPC1005X55
C50: 10n; CAPC1005X55
D3, D4, D5, D6: ACDBQC0130L-HF0402; DIOC1005X55N
IC14: SN74LV4T125PWR; PW0014A_N
IC15: LMP7701MF; DBV5-L
IC16: TXB0304RUTR; RUT0012A
R51: 24; RESC1005X40
R52: 10k; RESC1005X40

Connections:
+3V3: C46.1, C51.1, IC14.14 (VCC), IC16.11 (VCCB); also elsewhere on the board
EN_LVLCNV: IC16.12 (OE); also elsewhere on the board
GND: C46.2, C48.2, C49.2, C50.2, C51.2, IC14.1 (1OE_N), IC14.4 (2OE_N), IC14.7 (GND), IC14.10 (3OE_N), IC14.13 (4OE_N), IC15.2 (V-), IC16.6 (GND); also elsewhere on the board
GPIO0_BB: D5.2 (C); also elsewhere on the board
GPIO0_TARGET: IC14.12 (4A); also elsewhere on the board
GPIO1_BB: D3.2 (C); also elsewhere on the board
GPIO1_TARGET: IC14.5 (2A); also elsewhere on the board
GPIO2_BB: D6.2 (C); also elsewhere on the board
GPIO2_TARGET: IC14.9 (3A); also elsewhere on the board
GPIO3_BB: D4.2 (C); also elsewhere on the board
GPIO3_TARGET: IC14.2 (1A); also elsewhere on the board
unnamed: D4.1 (A), IC14.3 (1Y)
unnamed: C47.1, IC15.1 (OUT), R51.2, R52.1
unnamed: D3.1 (A), IC14.6 (2Y)
unnamed: D6.1 (A), IC14.8 (3Y)
unnamed: D5.1 (A), IC14.11 (4Y)
unnamed: C47.2, IC15.4 (IN-), R52.2
SWDCLK_BB: IC16.9 (B2); also elsewhere on the board
SWDCLK_TARGET: IC16.3 (A2); also elsewhere on the board
SWDIO_BB: IC16.10 (B1); also elsewhere on the board
SWDIO_TARGET: IC16.2 (A1); also elsewhere on the board
UART_RX_BB: IC16.7 (B4); also elsewhere on the board
UART_RX_TARGET: IC16.4 (A3); also elsewhere on the board
UART_TX_BB: IC16.8 (B3); also elsewhere on the board
UART_TX_TARGET: IC16.5 (A4); also elsewhere on the board
VDD: C48.1, IC15.5 (V+); also elsewhere on the board
VDD_TARGET: C50.1, IC16.1 (VCCA), R51.1
V_SUP_TARGET: C49.1, IC15.3 (IN+); also elsewhere on the board

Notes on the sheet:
Bi-directional level converter for UART and SWD signals
Uni-directional, high input impedance level converter for GPIO tracing
Voltage buffer for generating the supply voltage for the bi-directional level converter


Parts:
C26, C28, C52: 1u; CAPC1608X95
C27, C38, C53: 0.1u; CAPC1005X55
C36, C39, C40: 2.2u; CAPC2012X145
C37: 0.47u; CAPC1608X95
C41: 4.7u; CAPC2012X145
IC7: DAC6571IDBVR
IC8: TPS73101DBVR; SOT95P280X145-5N
IC11: CAT24C256WI-GT3; SO08
IC12: LM27762DSSR; VREG_LM27762DSSR
R22, R23, R47, R48, R49: 5.6k; RESC1005X40
R24: 56k; RESC1005X40
R25: 40.2k; RESC1005X40
R26: 30k; RESC1005X40
R43: 300k; RESC1005X40
R44, R46: 100k; RESC1005X40
R45: 294k; RESC1005X40
R50: 10k; RESC1005X40
S4: TMUX1101DCK; DCK5
TP5, TP6: TPSQTP06R; TP06R
WP: TPSQTP06R; TP06R

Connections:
+3V3: C26.1, C27.2, C38.1, IC7.3 (VDD), IC11.8 (VCC), R22.2, R23.2, R47.2, R48.2, R49.2, R50.2; also elsewhere on the board
+5V: C36.1, IC12.3 (VIN); also elsewhere on the board
EN_V_ANLG: IC12.8 (EN_N), IC12.12 (EN_P); also elsewhere on the board
EN_V_FIX: S4.4 (SEL); also elsewhere on the board
GND: C26.2, C27.1, C28.2, C36.2, C38.2, C39.2, C40.2, C41.2, C52.2, C53.2, IC7.2 (GND), IC7.6 (A0), IC8.2 (GND), IC11.1 (A0), IC11.2 (A1), IC11.4 (VSS), IC12.1 (PGOOD), IC12.4 (GND), IC12.13 (EP_GND), R26.2, R44.1, R46.1, S4.3 (GND); also elsewhere on the board
I2C1_SCL: IC7.5 (SCL), R22.1; also elsewhere on the board
I2C1_SDA: IC7.4 (SDA), R23.1; also elsewhere on the board
I2C2_SCL: IC11.6 (SCL), R47.1; also elsewhere on the board
I2C2_SDA: IC11.5 (SDA), R48.1; also elsewhere on the board
unnamed: C52.1, IC8.5 (OUT), R25.1, S4.1 (D)
unnamed: IC8.4 (NR/FB), R24.2, R25.2, R26.1
unnamed: IC12.2 (FB_P), R43.1, R44.2
unnamed: IC7.1 (VOUT), R24.1
unnamed: IC11.7 (WP), R50.1, WP.TP
unnamed: IC12.7 (FB_N), R45.1, R46.2
unnamed: IC11.3 (A2), R49.1
unnamed: C41.1, IC12.5 (CP)
unnamed: C37.2, IC12.9 (C1_N)
unnamed: C37.1, IC12.10 (C1_P)
VDD: C28.1, C40.1, C53.1, IC8.1 (IN), IC8.3 (EN), IC12.11 (OUT_P), R43.2, S4.5 (VDD), TP5.TP; also elsewhere on the board
VSS: C39.1, IC12.6 (OUT_N), R45.2, TP6.TP; also elsewhere on the board
V_LD_SHT+: S4.2 (S); also elsewhere on the board

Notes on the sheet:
Fixed supply voltage for programming/non-harvesting operation of the testbed. The DAC output voltage changes the voltage on the reference pin of the LDO, linearly controlling its output voltage.
Generates the low-noise, positive and negative analog supply voltages
EEPROM for storing BB cape info and calibration data


Board: 4 copper layers, 86.4 x 54.6 mm, 171 parts (0 on the bottom side), 134 nets.

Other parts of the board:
U$1, U$2, U$3: REFMARK

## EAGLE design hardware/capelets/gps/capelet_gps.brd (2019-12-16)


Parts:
C1: 22u; CAPC3225X280
C2, C3: 0.1u; CAPC2012X145
IC1: SAM-M8Q
P8, P9: PINHD-2X11; 2X11
PPS: 598-8130-107FLED_0805; LEDC2012X75
R1: 130R; RESC2012X65
T1: SI2374DSSOT23-VSHAY; SOT95P237X112-3

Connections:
+3V3: C1.1, C2.1, C3.1, IC1.2 (VCC_IO), IC1.3 (V_BCKP), IC1.17 (VCC), P9.3 (4), P9.4 (3), R1.2
GND: C1.2, C2.2, C3.2, IC1.1 (GND), IC1.4 (GND), IC1.5 (GND), IC1.6 (GND), IC1.10 (GND), IC1.11 (GND), IC1.15 (GND), IC1.16 (GND), IC1.20 (GND), P8.1 (2), P8.2 (1), P9.1 (2), P9.2 (1), T1.2 (S)
unnamed: PPS.1 (C), T1.3 (D)
unnamed: PPS.2 (A), R1.1
RESET_N: IC1.18 (RESET_N), P8.8 (7)
SAFEBOOT_N: IC1.8 (SAFEBOOT_N), P8.9 (10)
TIMEPULSE: IC1.7 (TP), P8.7 (8), T1.1 (G)
UART2_RX: IC1.13 (TXD), P9.22 (21)
UART2_TX: IC1.14 (RXD), P9.21 (22)



Board: 2 copper layers, 54.6 x 31.1 mm, 13 parts (2 on the bottom side), 9 nets.

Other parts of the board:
U$1, U$2, U$4: REFMARK
U$3: SHPRD_CPLT_G

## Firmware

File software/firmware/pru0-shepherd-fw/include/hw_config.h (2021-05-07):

#ifndef _HW_CONFIG_H_
#define _HW_CONFIG_H_

#include "gpio.h"

// asm-routine needs unshifted bit positions (_PIN)
#define SPI_CS_ADC_PIN     	(P9_25)
#define SPI_CS_ADC_MASK		BIT_SHIFT(SPI_CS_ADC_PIN)
#define SPI_CS_DAC_PIN      	(P9_31)
#define SPI_CS_DAC_MASK 	BIT_SHIFT(SPI_CS_DAC_PIN)

#define SPI_SCLK_MASK 		BIT_SHIFT(P9_28)
#define SPI_MOSI_MASK 		BIT_SHIFT(P9_30)
#define SPI_MISO_MASK 		BIT_SHIFT(P9_27)

#define DEBUG_PIN0_MASK 	BIT_SHIFT(P8_11)
#define DEBUG_PIN1_MASK 	BIT_SHIFT(P8_12)

#endif /* _HW_CONFIG_H_ */

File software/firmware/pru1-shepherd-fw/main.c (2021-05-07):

#include <stdint.h>
#include <stdbool.h>
#include <string.h>
#include <pru_cfg.h>
#include <pru_intc.h>
#include <pru_iep.h>
#include <gpio.h>

#include "rpmsg.h"
#include "iep.h"
#include "intc.h"

#include "commons.h"
#include "shepherd_config.h"
#include "stdint_fast.h"
#include "debug_routines.h"

/* The Arm to Host interrupt for the timestamp event is mapped to Host interrupt 0 -> Bit 30 (see resource_table.h) */
#define HOST_INT_TIMESTAMP_MASK (1U << 30U)
#define PRU_INT_MASK 		(1U << 31U)

#define DEBUG_PIN0_MASK         BIT_SHIFT(P8_41)
#define DEBUG_PIN1_MASK         BIT_SHIFT(P8_42)

#define GPIO_MASK		(0x0F)

#define SANITY_CHECKS		(0)	// warning: costs performance, but is helpful for dev / debugging

enum SyncState {
	IDLE,
	REPLY_PENDING
};

//static void fault_handler(const uint32_t shepherd_state, const char * err_msg) // TODO: use when pssp gets changed
static void fault_handler(const uint32_t shepherd_state, char * err_msg)
{
	/* If shepherd is not running, we can recover from the fault */
	if (shepherd_state != STATE_RUNNING)
	{
		printf(err_msg);
		return;
	}

	while (true)
	{
		printf(err_msg);
		__delay_cycles(2000000000U);
	}
}


static inline bool_ft receive_control_reply(volatile struct SharedMem *const shared_mem, struct CtrlRepMsg *const ctrl_rep)
{
	if (shared_mem->ctrl_rep.msg_unread >= 1)
	{
		if (shared_mem->ctrl_rep.identifier != MSG_SYNC_CTRL_REP)
		{
			/* Error occurs if something writes over boundaries */
			fault_handler(shared_mem->shepherd_state, "Recv_CtrlReply -> mem corruption?");
		}
		*ctrl_rep = shared_mem->ctrl_rep; // TODO: faster to copy only the needed 2 uint32
		shared_mem->ctrl_rep.msg_unread = 0;

		if (SANITY_CHECKS)
		{
			/* sanity-check of vars */
			static uint64_t prev_timestamp_ns = 0;
			if ((ctrl_rep->buffer_block_period > TIMER_BASE_PERIOD + 80000) || (ctrl_rep->buffer_block_period < TIMER_BASE_PERIOD - 80000))
				fault_handler(shared_mem->shepherd_state, "Recv_CtrlReply -> buffer_block_period out of limits");
			if ((ctrl_rep->analog_sample_period > SAMPLE_PERIOD + 10) || (ctrl_rep->buffer_block_period < SAMPLE_PERIOD - 10))
				fault_handler(shared_mem->shepherd_state, "Recv_CtrlReply -> analog_sample_period out of limits");
			const uint64_t time_diff = ctrl_rep->next_timestamp_ns - prev_timestamp_ns;
			if ((time_diff != BUFFER_PERIOD_NS) && (prev_timestamp_ns > 0)) {
				if (ctrl_rep->next_timestamp_ns == 0)
					fault_handler(shared_mem->shepherd_state, "Recv_CtrlReply -> next_timestamp_ns is zero");
				else if (time_diff > BUFFER_PERIOD_NS + 5000000)
					fault_handler(shared_mem->shepherd_state, "Recv_CtrlReply -> next_timestamp_ns is > 105 ms");
				else if (time_diff < BUFFER_PERIOD_NS - 5000000)
					fault_handler(shared_mem->shepherd_state, "Recv_CtrlReply -> next_timestamp_ns is < 95 ms");
				else
					fault_handler(shared_mem->shepherd_state, "Recv_CtrlReply -> timestamp-jump was not 100 ms");
			}
			prev_timestamp_ns = ctrl_rep->next_timestamp_ns;
		}
		return 1;
	}
	return 0;
}

// send emits a 1 on success
// ctrl_req: (future opt.) needs to have special config set: identifier=MSG_SYNC_CTRL_REQ and msg_unread=1
static inline bool_ft send_control_request(volatile struct SharedMem *const shared_mem, const struct CtrlReqMsg *const ctrl_req)
{
	if (shared_mem->ctrl_req.msg_unread == 0)
	{
		shared_mem->ctrl_req = *ctrl_req;
		shared_mem->ctrl_req.identifier = MSG_SYNC_CTRL_REQ; // TODO: is better done in request from argument
		// NOTE: always make sure that the unread-flag is activated AFTER payload is copied
		shared_mem->ctrl_req.msg_unread = 1u;
		return 1;
	}
	/* Error occurs if PRU was not able to handle previous message in time */
	fault_handler(shared_mem->shepherd_state, "Send_CtrlReq -> back-pressure");
	return 0;
}

/*
 * Here, we sample the the GPIO pins from a connected sensor node. We repeatedly
 * poll the state via the R31 register and keep the last state in a static
 * variable. Once we detect a change, the new value (V1=4bit, V2=10bit) is written to the
 * corresponding buffer (which is managed by PRU0). The tricky part is the
 * synchronization between the PRUs to avoid inconsistent state, while
 * minimizing sampling delay
 */
static inline void check_gpio(volatile struct SharedMem *const shared_mem, const uint32_t last_sample_ticks)
{
	static uint32_t prev_gpio_status = 0x00;

	/*
	* Only continue if shepherd is running and PRU0 actually provides a buffer
	* to write to.
	*/
	if ((shared_mem->shepherd_state != STATE_RUNNING) ||
	    (shared_mem->gpio_edges == NULL)) {
		prev_gpio_status = 0x00;
		return;
	}

	const uint32_t gpio_status = read_r31() & GPIO_MASK;
	const uint32_t gpio_diff = gpio_status ^ prev_gpio_status;

	prev_gpio_status = gpio_status;

	if (gpio_diff > 0)
	{
		DEBUG_GPIO_STATE_2;
		// local copy reduces reads to far-ram to current minimum
		const uint32_t cIDX = shared_mem->gpio_edges->idx;

		/* Each buffer can only store a limited number of events */
		if (cIDX >= MAX_GPIO_EVT_PER_BUFFER) return;

		/* Ticks since we've taken the last sample */
		const uint32_t ticks_since_last_sample = CT_IEP.TMR_CNT - last_sample_ticks;
		/* Calculate final timestamp of gpio event */
		const uint64_t gpio_timestamp_ns = shared_mem->last_sample_timestamp_ns + TIMER_TICK_NS * ticks_since_last_sample;

		simple_mutex_enter(&shared_mem->gpio_edges_mutex);
		shared_mem->gpio_edges->timestamp_ns[cIDX] = gpio_timestamp_ns;
		shared_mem->gpio_edges->bitmask[cIDX] = (uint8_t)gpio_status;
		shared_mem->gpio_edges->idx = cIDX + 1;
		simple_mutex_exit(&shared_mem->gpio_edges_mutex);
	}
}


/*
 * The firmware for synchronization/sample timing is based on a simple
 * event loop. There are three events: 1) Interrupt from Linux kernel module
 * 2) Local IEP timer wrapped 3) Local IEP timer compare for sampling
 *
 * Event 1:
 * The kernel module periodically timestamps its own clock and immediately
 * triggers an interrupt to PRU1. On reception of that interrupt we have
 * to timestamp our local IEP clock. We then send the local timestamp to the
 * kernel module as an RPMSG message. The kernel module runs a PI control loop
 * that minimizes the phase shift (and frequency deviation) by calculating a
 * correction factor that we apply to the base period of the IEP clock. This
 * resembles a Phase-Locked-Loop system. The kernel module sends the resulting
 * correction factor to us as an RPMSG. Ideally, Event 1 happens at the same
 * time as Event 2, i.e. our local clock should wrap at exactly the same time
 * as the Linux host clock. However, due to phase shifts and kernel timer
 * jitter, the two events typically happen with a small delay and in arbitrary
 * order. However, we would
 *
 * Event 2:
 *
 * Event 3:
 * This is the main sample trigger that is used to trigger the actual sampling
 * on PRU0 by raising an interrupt. After every sample, we have to forward
 * the compare value, taking into account the current sampling period
 * (dynamically adapted by PLL). Also, we will only check for the controller
 * reply directly following this event in order to avoid sampling jitter that
 * could result from being busy with RPMSG and delaying response to the next
 * Event 3
 */

int32_t event_loop(volatile struct SharedMem *const shared_mem)
{
	uint32_t last_analog_sample_ticks = 0;

	/* Prepare message that will be received and sent to Linux kernel module */
	struct CtrlReqMsg ctrl_req = { .identifier = MSG_SYNC_CTRL_REQ, .msg_unread = 0u };
	struct CtrlRepMsg ctrl_rep = {
		.buffer_block_period = TIMER_BASE_PERIOD,
		.analog_sample_period = TIMER_BASE_PERIOD / ADC_SAMPLES_PER_BUFFER,
		.compensation_steps = 0u,
	};

	/* This tracks our local state, allowing to execute actions at the right time */
	enum SyncState sync_state = IDLE;

	/*
	* This holds the number of 'compensation' periods, where the sampling
	* period is increased by 1 in order to compensate for the remainder of the
	* integer division used to calculate the sampling period.
	*/
	uint32_t compensation_steps = ctrl_rep.compensation_steps;
	/*
	 * holds distribution of the compensation periods (every x samples the period is increased by 1)
	 */
	uint32_t compensation_counter = 0u;
	uint32_t compensation_increment = 0u;

	/* Our initial guess of the sampling period based on nominal timer period */
	uint32_t analog_sample_period = ctrl_rep.analog_sample_period;
	uint32_t buffer_block_period = ctrl_rep.buffer_block_period;

	/* These are our initial guesses for buffer sample period */
	iep_set_cmp_val(IEP_CMP0, TIMER_BASE_PERIOD);  // 20 MTicks -> 100 ms
	iep_set_cmp_val(IEP_CMP1, buffer_block_period); // 20 kTicks -> 10 us

	iep_enable_evt_cmp(IEP_CMP1);
	iep_clear_evt_cmp(IEP_CMP0);

	/* Clear raw interrupt status from ARM host */
	INTC_CLEAR_EVENT(HOST_PRU_EVT_TIMESTAMP);
	/* Wait for first timer interrupt from Linux host */
	while (!(read_r31() & HOST_INT_TIMESTAMP_MASK)) {};

	if (INTC_CHECK_EVENT(HOST_PRU_EVT_TIMESTAMP)) INTC_CLEAR_EVENT(HOST_PRU_EVT_TIMESTAMP);

	iep_start();

	while (1)
	{

		#if DEBUG_LOOP_EN
		debug_loop_delays(shared_mem->shepherd_state);
		#endif

		DEBUG_GPIO_STATE_1;
		    check_gpio(shared_mem, last_analog_sample_ticks);
		DEBUG_GPIO_STATE_0;

		/* [Event1] Check for interrupt from Linux host to take timestamp */
		if (read_r31() & HOST_INT_TIMESTAMP_MASK)
		{
			if (!INTC_CHECK_EVENT(HOST_PRU_EVT_TIMESTAMP)) continue;

			/* Take timestamp of IEP */
			ctrl_req.ticks_iep = iep_get_cnt_val();
			DEBUG_EVENT_STATE_2;
			/* Clear interrupt */
			INTC_CLEAR_EVENT(HOST_PRU_EVT_TIMESTAMP);

			if (sync_state == IDLE)    sync_state = REPLY_PENDING;
			else {
				fault_handler(shared_mem->shepherd_state,"Sync not idle at host interrupt");
				return 0;
			}
			send_control_request(shared_mem, &ctrl_req);
			DEBUG_EVENT_STATE_0;
			continue;  // for more regular gpio-sampling
		}

		/*  [Event 2] Timer compare 0 handle -> trigger for buffer swap on pru0 */
		if (shared_mem->cmp0_trigger_for_pru1)
		{
			DEBUG_EVENT_STATE_2;
			// reset trigger
			shared_mem->cmp0_trigger_for_pru1 = 0;

			/* update clock compensation of sample-trigger */
			iep_set_cmp_val(IEP_CMP1, 0);
			iep_enable_evt_cmp(IEP_CMP1);
			analog_sample_period = ctrl_rep.analog_sample_period;
			compensation_steps = ctrl_rep.compensation_steps;
			compensation_increment = ctrl_rep.compensation_steps;
			compensation_counter = 0;

			/* update main-loop */
			buffer_block_period = ctrl_rep.buffer_block_period;
			iep_set_cmp_val(IEP_CMP0, buffer_block_period);

			/* more maintenance */
			last_analog_sample_ticks = 0;

			DEBUG_EVENT_STATE_0;
			continue; // for more regular gpio-sampling
		}

		/* [Event 3] Timer compare 1 handle -> trigger for analog sample on pru0 */
		if (shared_mem->cmp1_trigger_for_pru1)
		{
			/* prevent a race condition (cmp0_event has to happen before cmp1_event!) */
			if (shared_mem->cmp0_trigger_for_pru1) continue;

			DEBUG_EVENT_STATE_1;
			// reset trigger
			shared_mem->cmp1_trigger_for_pru1 = 0;

			// Update Timer-Values
			last_analog_sample_ticks = iep_get_cmp_val(IEP_CMP1);
			if (last_analog_sample_ticks > 0) // this assumes sample0 taken on cmp1==0
			{
				shared_mem->last_sample_timestamp_ns += SAMPLE_INTERVAL_NS;
			}

			/* Forward sample timer based on current analog_sample_period*/
			uint32_t next_cmp_val = last_analog_sample_ticks + analog_sample_period;
			compensation_counter += compensation_increment; // fixed point magic
			/* If we are in compensation phase add one */
			if ((compensation_counter >= ADC_SAMPLES_PER_BUFFER) && (compensation_steps > 0)) {
				next_cmp_val += 1;
				compensation_steps--;
				compensation_counter -= ADC_SAMPLES_PER_BUFFER;
			}
			iep_set_cmp_val(IEP_CMP1, next_cmp_val);
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

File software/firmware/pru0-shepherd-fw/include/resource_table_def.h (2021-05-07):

/*
 * Copyright (C) 2016 Texas Instruments Incorporated - http://www.ti.com/
 *
 *
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
 *	* Redistributions of source code must retain the above copyright
 *	  notice, this list of conditions and the following disclaimer.
 *
 *	* Redistributions in binary form must reproduce the above copyright
 *	  notice, this list of conditions and the following disclaimer in the
 *	  documentation and/or other materials provided with the
 *	  distribution.
 *
 *	* Neither the name of Texas Instruments Incorporated nor the names of
 *	  its contributors may be used to endorse or promote products derived
 *	  from this software without specific prior written permission.
 *
 * THIS SOFTWARE IS PROVIDED BY THE COPYRIGHT HOLDERS AND CONTRIBUTORS
 * "AS IS" AND ANY EXPRESS OR IMPLIED WARRANTIES, INCLUDING, BUT NOT
 * LIMITED TO, THE IMPLIED WARRANTIES OF MERCHANTABILITY AND FITNESS FOR
 * A PARTICULAR PURPOSE ARE DISCLAIMED. IN NO EVENT SHALL THE COPYRIGHT
 * OWNER OR CONTRIBUTORS BE LIABLE FOR ANY DIRECT, INDIRECT, INCIDENTAL,
 * SPECIAL, EXEMPLARY, OR CONSEQUENTIAL DAMAGES (INCLUDING, BUT NOT
 * LIMITED TO, PROCUREMENT OF SUBSTITUTE GOODS OR SERVICES; LOSS OF USE,
 * DATA, OR PROFITS; OR BUSINESS INTERRUPTION) HOWEVER CAUSED AND ON ANY
 * THEORY OF LIABILITY, WHETHER IN CONTRACT, STRICT LIABILITY, OR TORT
 * (INCLUDING NEGLIGENCE OR OTHERWISE) ARISING IN ANY WAY OUT OF THE USE
 * OF THIS SOFTWARE, EVEN IF ADVISED OF THE POSSIBILITY OF SUCH DAMAGE.
 */

#ifndef _RSC_TABLE_PRU_H_
#define _RSC_TABLE_PRU_H_

#include <stddef.h>

#include "pru_virtio_ids.h"
#include "resource_table.h"
#include "commons.h"
#include "ringbuffer.h"

/*
 * Sizes of the virtqueues (expressed in number of buffers supported,
 * and must be power of 2)
 */
#define PRU_RPMSG_VQ0_SIZE  64U
#define PRU_RPMSG_VQ1_SIZE  64U

/*
 * The feature bitmap for virtio rpmsg
 */
#define VIRTIO_RPMSG_F_NS   0U // name service notifications

/* This firmware supports name service notifications as one of its features */
#define RPMSG_PRU_C0_FEATURES (1U << VIRTIO_RPMSG_F_NS)

/* Definition for unused interrupts */
#define HOST_UNUSED     255U

/* Mapping sysevts to a channel. Each pair contains a sysevt, channel. */
struct ch_map pru_intc_map[] = {
	{ PRU_PRU_EVT_SAMPLE, 1 }, // previous message-system between PRUs, TODO: test of reinsert to find pru-hickups
	{ PRU_PRU_EVT_BLOCK_END, 1 }, // previous message-system between PRUs
	{ 16, 3 }  // TODO: what is that for? is it "Interrupt for sync from ARM host"?
};

#define SIZE_CARVEOUT	(RING_SIZE * sizeof(struct SampleBuffer))

// pseudo-assertion to test for correct struct-size, zero cost
extern uint32_t CHECK_CARVEOUT[1/(SIZE_CARVEOUT >= 64 * (8 + 4 + 2*4*10000 + 4 + 8*16384 + 1*16384))];
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

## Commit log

2019-06-20 hardware: initial commit
    [cape.brd, cape.sch, capelet_gps.brd, capelet_gps.sch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]
2019-06-26 added shepherd device tree overlay
2019-07-04 travis: print some debug info
2019-07-04 firmware: fixed number of samples vs number of values bug in definition of buffer struct
2019-07-05 hardware: fixed wrong part number for constant supply LDO
    [cape.brd, cape.sch]
2019-07-05 python-package: updated default calibration to hardware rev 1.3
2019-07-06 hardware: fixed direction of level-converter
    [cape.brd, cape.sch]
2019-07-06 hardware: moved storage capelet to fit outline
    [cape.brd]
2019-07-06 python-package: allow setting harvesting voltage as actual voltage
2019-07-06 python-package: docstrings for calibration module
2019-07-08 python-package: detect faulty calibration data and gently fall back to defaults
2019-07-09 Bump version: 0.0.1 → 0.0.2
2019-07-10 Bump version: 0.0.2 → 0.0.3
2019-07-10 Bump version: 0.0.3 → 0.0.4
2019-07-11 Bump version: 0.0.4 → 0.0.5
2019-07-11 firmware: keep LED switched off if nothing is happening
2019-07-14 hardware: storage capelet: added labels to the pin headers
    [capelet_storage.brd, capelet_storage.sch]
2019-07-14 software: openocd: don't handle node power supply in systemd service - this should be handleded externally
2019-07-16 Bump version: 0.0.5 → 0.0.6
2019-07-16 Bump version: 0.0.6 → 0.0.7
2019-07-16 Bump version: 0.0.7 → 0.0.8
2019-07-17 Bump version: 0.0.8 → 0.0.9
2019-08-07 hardware: gps capelet: added component values and BOM
    [bom.csv, capelet_gps.brd, capelet_gps.sch]
2019-08-14 Started on adding virtcap, changed ERR log, added pin P9_29
2019-08-28 shepherd-herd: pre-charge capacitor by default
2019-08-28 shepherd-herd: fixed hostname print bug
2019-09-02 added support for variable voltage linear regulator
2019-09-06 integrated constant voltage regulator code with API
2019-09-11 cli: allow setting fixed target supply voltage with 'targetpower' command
2019-09-11 tests: separate tests for each CLI call to workaround testing framework issues
2019-09-11 firmware: use debug pins to mark sample and block edges on PRU1
2019-09-11 Bump version: 0.0.9 → 0.1.0
2019-09-18 Got virtcap working with actual adc sample values
2019-09-25 Changed the shepherd kernel-module to a platform-driver to make a robust solution by replacing the get-pru-phandle process. The necessary informations are extracted through the shepherd-device-tree o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
    Please note it is very important that the device-tree-overlay is loaded through the dtb_overlay in the /boot/uEnv.txt tag to work properly.
    This commit resolves Issue: #7
2019-09-26 hardware: cape: reverted to BQ25504, fixed booting bug and added logo
    [cape.brd, cape.sch]
2019-09-26 hardware: cape: added BOM and assembly plan for BETA layout
    [bom_beta_layout.csv]
2019-10-09 wip on integrating setting calibration settings in python code
2019-10-10 worked on sysfs calibrationsettings. get error when executed
2019-10-10 continued on calibration settings integration
2019-10-24 hardware: updated capelets
    [capelet_kinetic.brd, capelet_kinetic.sch, capelet_nrf52.brd, capelet_nrf52.sch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]
2019-10-24 hardware: fixed wrong part number in Beta BOM for ROK3
    [bom_beta_layout.csv]
2019-11-01 hardware: fancy frames around capelet schematics
    [capelet_kinetic.sch, capelet_nrf52.sch, capelet_solar.brd, capelet_solar.sch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]
2019-11-05 hardware: fancy frames for cape schematics
    [cape.sch]
2019-11-05 Bump version: 0.1.0 → 0.1.1
2019-11-06 fixed using calibration settings, some cleenup still needed
2019-11-15 Added downsampling of output voltage
2019-11-25 removed debug statements from code, added more comments, removed some prints in python, continued on dev documentation, added shepherd-herd support
2019-11-26 Fixed setting proper LDO voltage according to virtcap settings, fixed wrong return statement
2019-11-27 removing redundant scripts, re-enable Raise missing Sample error, removing probable unwanted changes to shepherd
2019-12-10 added logo files
    [logo.dxf]
2019-12-11 added initial script for calibration using Keithley SMU
2019-12-14 hardware: revised GPS capelet
    [bom.csv, capelet_gps.brd, capelet_gps.sch]
2019-12-14 hardware: replaced LDO diode with switch connected to PRU+ARM. Added connector for illuminated button.
    [bom_beta_layout.csv, cape.brd, cape.sch]
2019-12-16 hardware: prepared GPS capelet for professional assembly
    [bom.csv, bom_beta_layout.csv, capelet_gps.brd, capelet_gps.sch]
2019-12-16 hardware: minor revisions on cape silkscreen
    [cape.brd]
2019-12-17 python-package: fixed button LED default gpio number
2019-12-20 device-tree: Added overlay for virtcap mode
2019-12-21 firmware: included virtcap device tree in makefile
2020-01-05 hardware: prepared capelets for external manufacturing
    [capelet_kinetic.brd, capelet_kinetic.sch, capelet_nrf52.brd, capelet_nrf52.sch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]
2020-01-13 Bump version: 0.1.1 → 0.2.0
2020-08-03 device-tree: switch order of button/led pin
2020-08-03 add pdfs of current schematics
2020-08-03 fix device tree overlay
2020-08-03 fix example for current py code
2020-10-14 improve device tree drivers
2020-10-15 optimize printf
    fixed width ints, const correctness, optimal data type, better naming
2020-10-15 Update hw_config.h
    cleaner and faster pin access
2020-10-15 bring back previous led-behaviour
2020-10-16 added housings for shepherd hardware and piezo harvester
    [clamp_powerbank_belt.stl, piezo_harvester_case.stl, piezo_harvester_clamp.stl, piezo_harvester_cover.stl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]
2020-10-16 hardware: WIP: rf harvesting capelet
    [capelet_rf.brd, capelet_rf.sch]
2020-10-16 plot.py: use proper downsampling with low-pass filter
2020-10-16 Bump version: 0.2.0 → 0.2.1
2020-10-19 Bump version: 0.2.1 → 0.2.2
2020-11-03 extend iep-device
    to better compensate slow reads
2020-11-03 Bump version: 0.2.2 → 0.2.3
2020-11-04 second stage of ansible fixes
    ansible 3 is more strict
2020-11-04 use new format for DT-Pin-Config
2020-11-05 Bump version: 0.2.3 → 0.2.4
2020-11-06 Update datalog.py
    revert paramter for compression-filter
2020-11-06 Bump version: 0.2.4 → 0.2.5
2020-11-09 Bump version: 0.2.5 → 0.2.6
2021-01-07 first stage of preparing pru0 for V2
2021-04-20 Update calibration_default.py
    add units and fix conversion-formulars
